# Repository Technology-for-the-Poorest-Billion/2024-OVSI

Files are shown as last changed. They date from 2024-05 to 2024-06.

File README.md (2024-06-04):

# OVSI Usage Monitoring Project

The Oxygen and Ventilator System Initiative (OVSI) "wants to ensure every individual has reliable and equitable access to essential medical oxygen". One of their key innovation domains is in developing a remote monitoring system that can integrate with all types of existing concentrators to track usage and schedule preventive maintenance. Our project looks at performing early stage testing relating to the various different sensors that could be used, and attempting to develop an early prototype. The output from this mini-project should help to give preliminary results and insights into the viablility of the different routes that could be taken to develop a non-invasive monitoring device.

Below is a brief explanation of what is contained in each folder:
- `1. project_proposal` contains both the project proposal and project management information
- `2. interim_report` contains a markdown document containing the interim report for this project
- `3. final_output` contains documentation of the project output which are also the handover notes for the project partner OVSI.
- `4. code` contains all code used throughout the project. It has folders for both the Micropython code used with a Pi Pico and the Python code for reading the output from various sensors through the serial port.
- `5. test_data` contains all of the datasets and results from any testing we performed
- `www` contains the markdown documents which are converted into HTML for our website

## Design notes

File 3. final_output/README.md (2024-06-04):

# OVSI Final Output folder

This folder contains all of the handover notes to be given to Ben and the team at OVSI. This contains a summary of the project, with all the required aspects covered to understand and recreate the prototype. 

Below is a brief explanation of what is contained in each folder:
- `1_prototype_demonstration` contains a demonstration of all functions of the final prototype.
- `2_hardware_and_circuitry` contains the breadboard layout and information on the sensor attachments, including the STL file for the 3D-printed clips.
- `3_code` contains both the Micropython code for the Pi Pico and Python code for reading the output of the sensors through the serial port, and converting it into a live interface.
- `4_further_considerations` contains a markdown document for suggestion for the next steps of the project, including ideas for refinement of the prototype, and further research that could be conducted.
- `5_testing_results` contains the results of the tests performed on the accelerometer and microphone used in producing the final prototype.
- `6_final_presentation` contains a .pdf file containing the slides to our final powerpoint presentation. The .mp4 video of the presentation is too large to attach here, but can be found on the final project submission to the project supervisor.

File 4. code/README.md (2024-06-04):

# Code documentation

The `accelerometer_code` folder contains any code which relates to the testing of the accelerometer.

The `microphone_code` folder contains any code which relates to the testing of the microphone.

The `combined_sensors_code` folder contains any code which relates to the testing of the device when both the accelerometer and the microphone were attached.

All code contains a description of the function of the code at the top of the file.

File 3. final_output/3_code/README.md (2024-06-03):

# Final Prototype Code

This folder contains the code needed to run the final prototype.

`main_combined_sensors.py` contains the micropython code that is used on the Raspberry Pi Pico to take the accelerometer output, and convert it into the accelerometer magnitude. It also takes the analogue microphone signal and converts it into a noise reading on a scale of 1-10.

`final_prototype.py` contains the python code to be used on a laptop to read the Pi Pico output through the serial port. There is a description of the code functionality at the top of the code.

The circuit needed to run the code is shown in the `hardware_and_circuitry.md` file.

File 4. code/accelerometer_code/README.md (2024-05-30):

# Code documentation

The `pico_micropython_code` folder contains the Micropython code that has been used on the Raspberry Pi Pico WH microcontroller. The top of every `.mpy` file will contain a brief description of what the code achieves.

The `python_read_from_serial` folder contains any Python code that reads the output from the serial port when the Pi Pico is attached to a laptop. Every `.py` file will contain a brief description of the purpose of the code at the top of the file, as well as which `.mpy` code it should be run with.

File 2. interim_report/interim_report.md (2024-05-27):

# Interim Presentation

### Work we have achieved to date

- Background reading on other similar applications of non-intrusive load monitoring. 
- Settled on our most promising idea for achieving monitoring using vibration sensing.
- Connected accelerometer to microcontroller.
- Written code to read and manipulate accelerometer data.
- Connected LED circuit to give visual interpretation of data.
- 3D printed mounting solution for breadboard. 
- Tested the vibration readings under a variety of conditions to help determine our measurement approach to monitoring.
- Data analysis of vibration readings.
- Developed and tested some prototype code using Matplotlib to determine and show whether or not the concentrator is on or off.

# Setup and Testing

### Setting up the accelerometer

To allow the Rasberry Pi Pico to read the accelerometer outputs, we first soldered pins onto the accelerometer so that we could connect it to the breadboard. We then attached the pico and accelerometer onto the breadboard and connected them together using jumper wires between the following pins:
 
 - **2-5V** on accelerometer to **3V3(OUT)** on pico.
 - **SDA** on accelerometer to **I2C1 SDA** on pico.
 - **SCL** on accelerometer to **I2C1 SCL** on pico.
 - **GND** on accelerometer to **GND** on pico.

Reading the output:

The next step was to be able to read the outputs from the accelerometer. This was done using an early version of the code main_interim_prototype.mpy and we were able to read the outputs using Thonny. It returned values of the x, y and z components of the acceleration as well as the magnitude.
In order to plot and visualise the accelerometer outputs we used Python in VS Code to read the serial output and create a live plot using the Matplotlib animation function. An example of this plot can be seen in Figure 1 below.

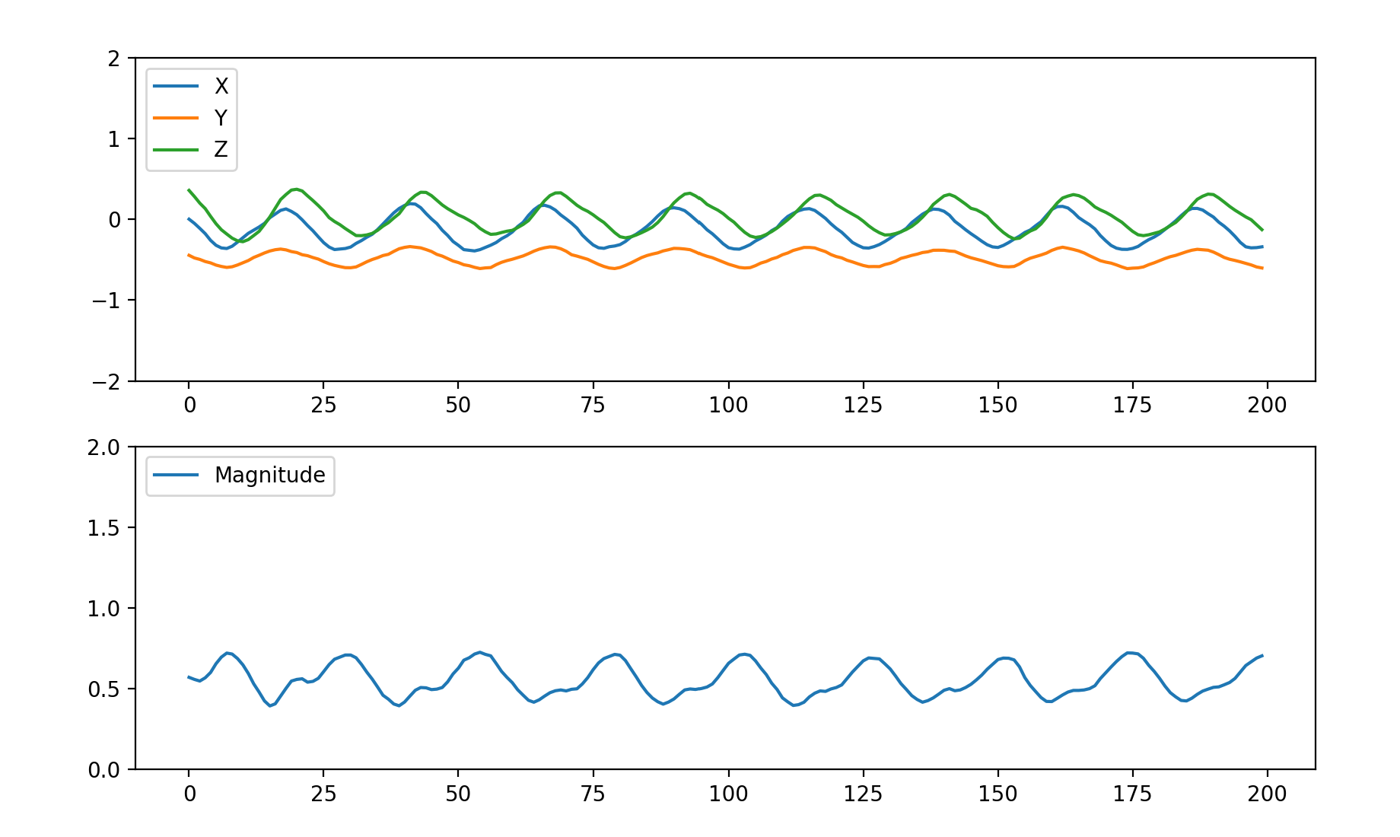
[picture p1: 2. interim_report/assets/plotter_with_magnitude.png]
Screenshot of python plotter


**Figure 1:** Screenshot of the python script plotting the x, y, z components from the accelerometer as well as the magnitude (measured in 'g'). The scale at the bottom shows the last 200 readings (i.e. 2 seconds).

Next we attempted to remove the gravitational component of the reading on the accelerometer by using the inbuilt gyros. We tried various filters and algorithms but were unable to find a simple enough solution, and so to avoid wasting time we decided simply to assume the sensor always remains vertical, and remove a value of 1g from the z output.

### Testing and Results

In order to test our accelerometer under the same conditions each time, it was important to create a system to mount the breadboard to the concentrator. Using a CAD design and 3D printing, we made clips that are glued to the plastic casing and allowed the breadboard to be attached and removed easily. See clip.STL in the assets file.

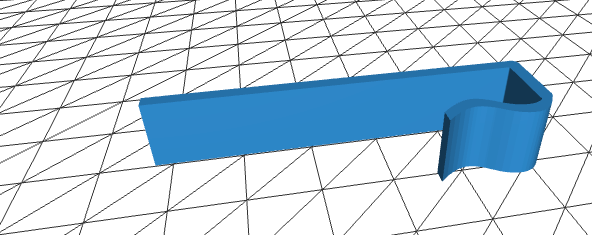
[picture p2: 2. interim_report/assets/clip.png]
clip.STL


We then ran tests to see if we could find a suitable vibration threshold that would indicate if the oxygen concentrator was being used. To do this we ran six different experiments, where we measured the vibrations:
- when the concentrator was turned on
- when the concentrator was turned off with no noise
- when the concentrator with the sensor attached was turned off, but the other concentrator was turned on and touching it
- when the concentrator with the sensor attached was turned off, but the other concentrator was turned on and 10cm away from it
- when the concentrator with the sensor attached was turned off, but we continuously rolled a trolley past and simulated heavy footfall
- when the concentrator with the sensor attached was turned off, but we put the front wheels on blocks to simulate being on uneven ground

Each test was run for 120 seconds. We then took the data and calculated the value of every rolling 10s mean and standard deviation. On the graphs we then plotted the smallest value of the rolling mean and standard deviation for the baseline-on test, and then the largest of the mean and standard deviation for the other test cases. 

Figure 2 below shows the results from when the accelerometer was attached to the black (significantly louder) concentrator. This shows that both the mean magnitude of vibration and the standard deviation when the concentrator is on can be easily differentiated from the other cases. 

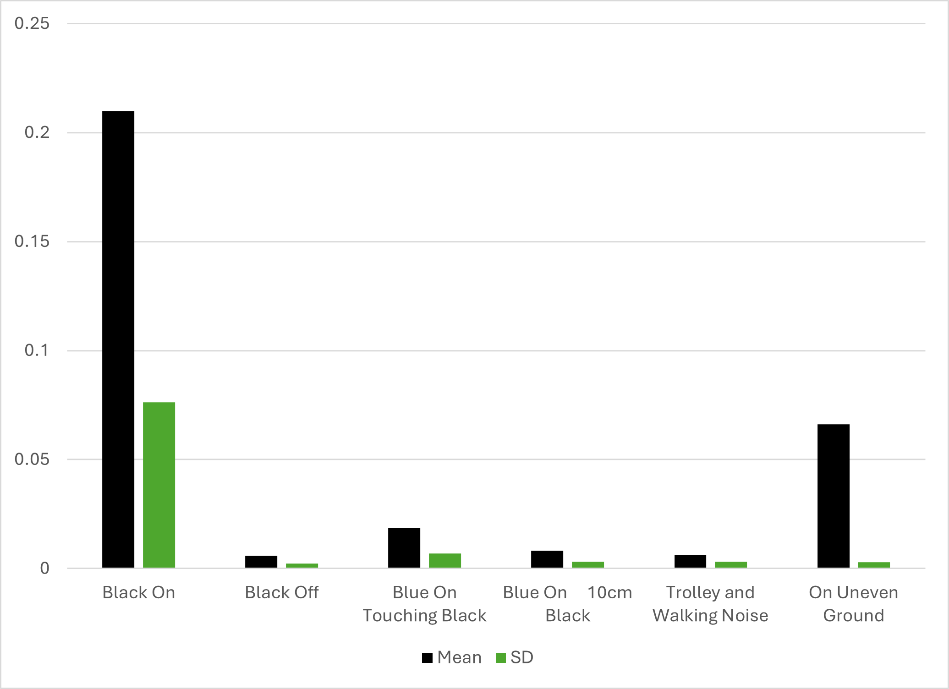
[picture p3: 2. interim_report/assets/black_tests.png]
bar chart of tests on black concentrator


**Figure 2:** Bar chart from the testing performed on the black concentrator.  

However, the Figure 3 below tells a different story. The blue EverFlo concentrator is significantly more quiet - 43dB rather than 69dB for the black one. The most common concentrators used in the target market are 40-50dB, so this is more indicative of the results we would expect to see during service. Here the results show that the mean and standard deviation for the test cases is of a similar or greater magnitude to the baseline-on case. This makes detection more difficult. Having the powerful black concentrator turned on next to the blue one gives comparable values to when the blue concentrator is in the on state and so could give false readings. Furthermore, uneven ground gives large readings for the magnitude, so any unexpected placement of the concentrator could give false readings. Also the standard deviation for the baseline-off test was much larger than expected, and after further analysis this was due to just a few larger values, which shows the ability of short impacts to the concentrator to spike the standard deviation reading.

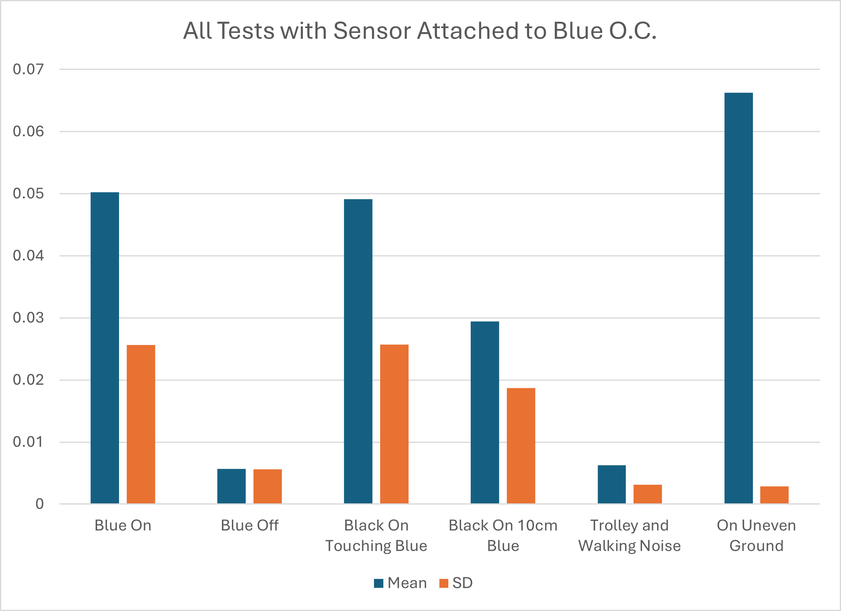
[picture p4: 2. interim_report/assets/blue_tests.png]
bar chart of tests on blue concentrator


**Figure 3:** Bar chart from the testing performed on the blue concentrator.  

Figure 4 shows the relative readings from the tests performed on the two oxygen concentrators, this shows that any strongly vibrating machinery placed nearby to the blue concentrator could result in false readings, whereas for the black concentrator it is much easier to differentiate the on and off state. This is something we plan to test further in order to better understand the likelihood and severity of this case in practice.

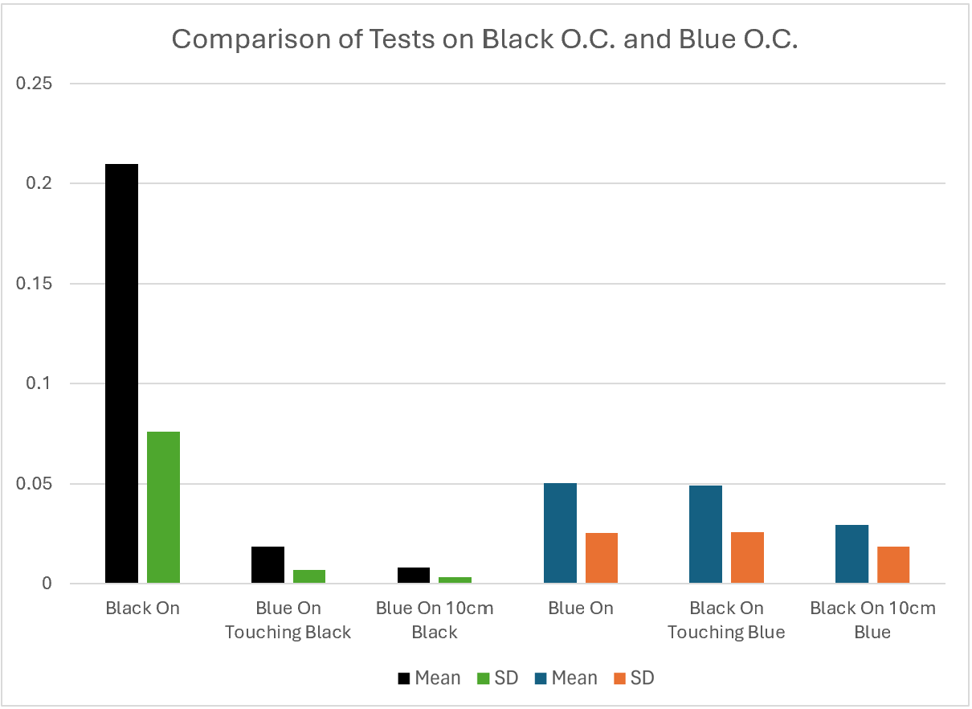
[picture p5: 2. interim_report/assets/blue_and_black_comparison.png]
bar chart comparing tests on black and blue concentrator


**Figure 4:** Bar chart comparing the results from the black and blue concentrators.  

The charts above have clearly demonstrated that being on uneven ground can give large mean value readings but very low standard deviation, as it is a steady state error. A sudden impact on the concentrator is enough to push the standard deviation over the expected value but due to the 10 second moving average it does not cause a dramatic increase in the average magnitude. This resulted in the implementation of a double threshold system where both magnitude and standard deviation were required to be above their threshold value for the device to recognise the concentrator as on. Tests below show the success of this new system.

Using these results we initially attempted to code the double threshold system directly onto the Raspberry Pi Pico, using an integrated LED circuit. Whilst we managed to get it working for the mean threshold, when we added in the standard deviation data we had memory storage issues. For this reason the 'prototype' discussed in the next section takes the accelerometer readings from the serial port and then does all the calculations and analysis in Python on a laptop.

# Prototype

### How it works

- Our 'prototype' Python code takes the readings of the magnitude of acceleration as measured by the accelerometer, and finds the mean and standard deviation of the last 1000 readings (i.e. 10 seconds).
- Every time a new reading comes in, the mean and standard deviation values are updated and then compared to a threshold. The thresholds have been determined from the testing done in the previous section. These thresholds determine whether or not the code thinks that the concentrator is currently turned on or off.
- In order to visualise this information, we have used the Matplotlib.animation function to plot the updated mean and standard deviation every time a new reading is taken. The plot shows the last 200 updated readings.
- The thresholds that are set for the mean and standard deviation are also plotted on the graph for easy viewing. When both thresholds are met the screen will turn green to show that the oxygen concentrator is running. If one or both of the outputs are below their respective thresholds then the screen will be red, indicating that the concentrator is not running. 

### Demonstration
All of the following data and graphics have been produced from testing performed with the accelerometer attached to the blue oxygen concentrator (the quieter of the two).
Figure 5 shows the Matplotlib output when the blue concentrator is turned on. Both the mean and standard deviation of the accelerometer readings are above the predetermined threshold and so the screen has turned green.

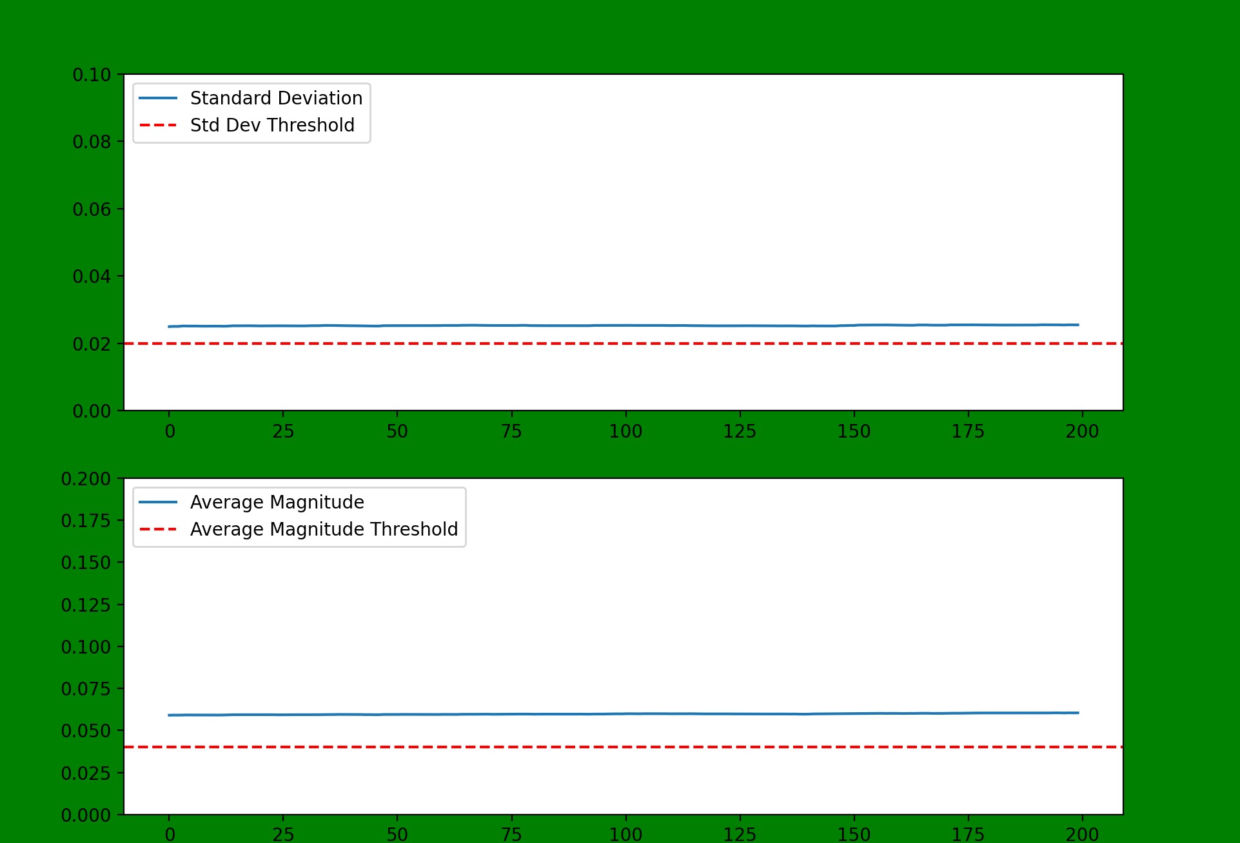
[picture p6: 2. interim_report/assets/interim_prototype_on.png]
screenshot of prototype with blue conc on


**Figure 5:** Prototype output when the blue concentrator is turned on.  

Figure 6 shows how the mean and standard deviation are affected by large knock to the concentrator. This noise is enough to send the standard deviation reading well over the threshold, but the mean stays comfortably below, and so the screen stays red.

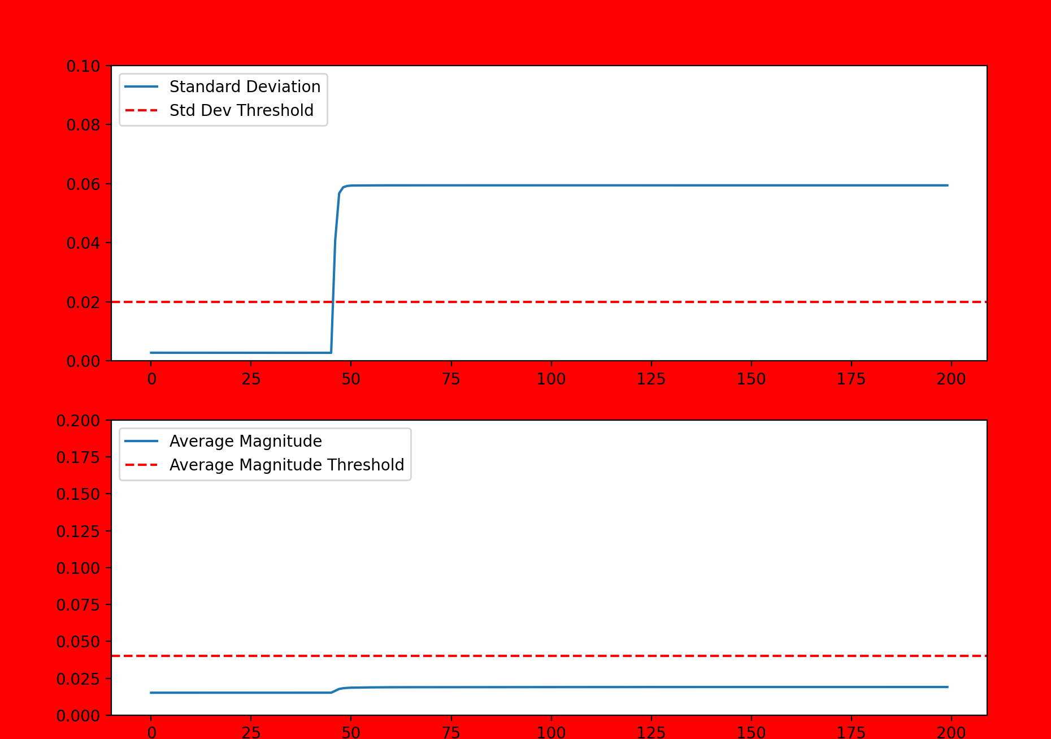
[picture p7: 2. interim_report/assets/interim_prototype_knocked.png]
screenshot of prototype with knock


**Figure 6:** Prototype output when the blue concentrator is turned off and knocked.  

Figure 7 shows the effect of leaving the concentrator on an uneven surface and during this measurement the concentrator was turned off. It is clear that the mean reading is well above the threshold due to gravity affecting the accelerometer readings. However, the standard deviation remains close to zero and so because this threshold is not met, the screen remains red.

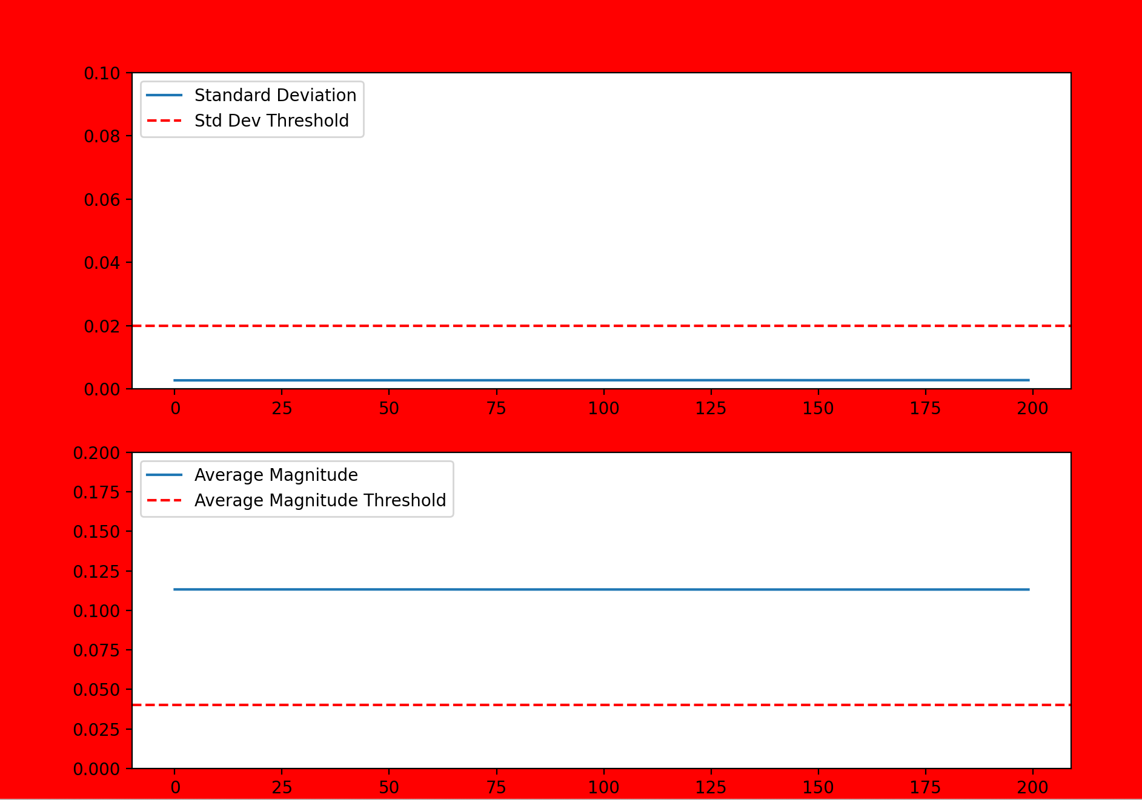
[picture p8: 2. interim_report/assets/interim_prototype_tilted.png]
screenshot of prototype with blue on tilt


**Figure 7:** Prototype output when the blue concentrator is turned off and placed on uneven ground.  

Figure 8 shows the Matplotlib interface when the blue concentrator is turned off, but the noisy black concentrator is turned on next to it and making direct contact. Whilst the readings are clearly above zero neither threshold is met and so the screen is red to show that the concentrator is not running.

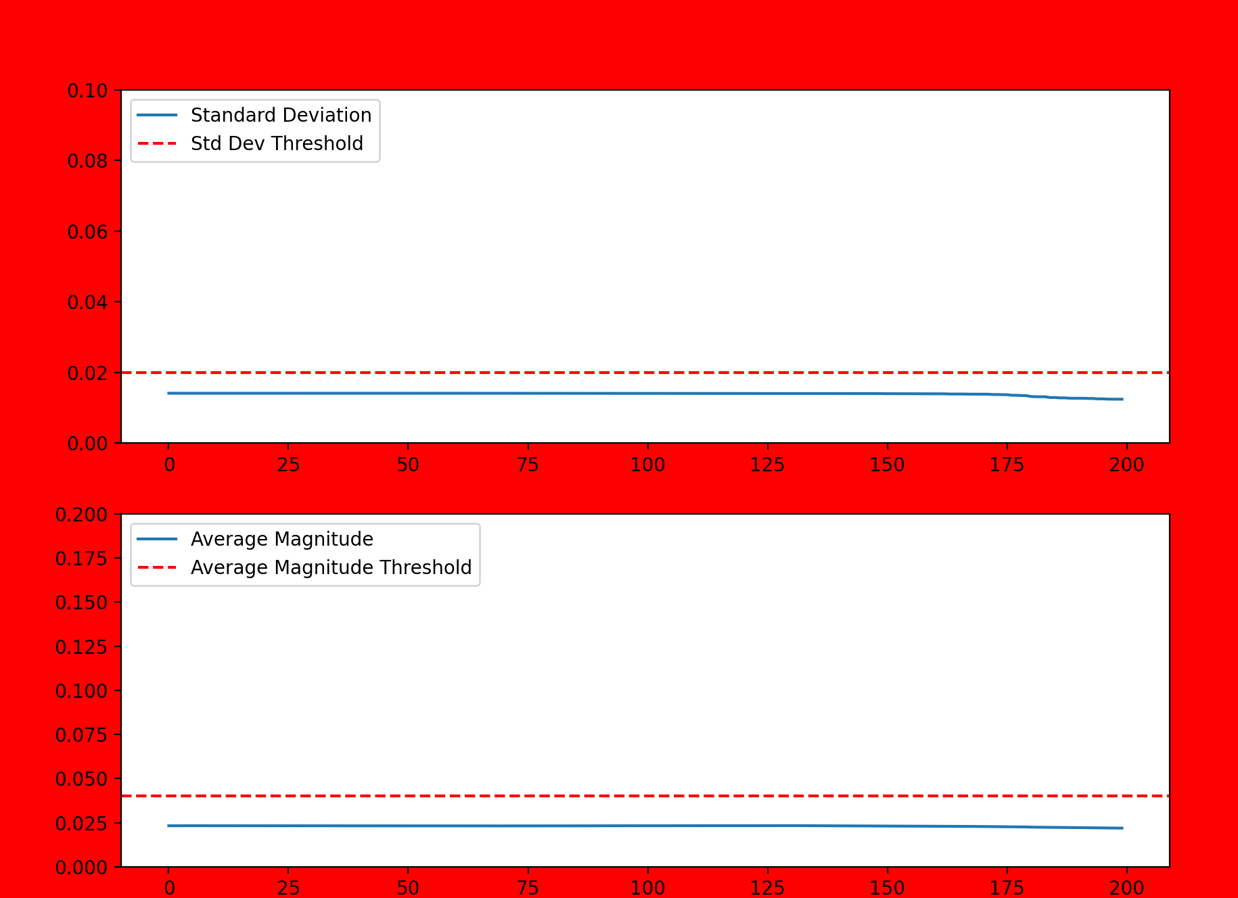
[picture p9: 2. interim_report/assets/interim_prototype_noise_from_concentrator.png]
screenshot of prototype with black on next to blue


**Figure 8:** Prototype output when the blue concentrator is turned off, and the black concentrator is turned on and touching. 

Below is a demonstration video of the above tests being performed.

https://github.com/Technology-for-the-Poorest-Billion/2024-OVSI/assets/98593139/cfc9f4a7-5daf-4990-bf7b-f4c7b06e2e5d

By using python to manipulate and plot the readings from the accelerometer it allowed for much easier analysis of how the monitoring system was working. However, once we had the above system in place, it was possible to try and convert the concept back into MicroPython code and use it alongside the LED circuit once again. This is now running successfully, and follows the exact same concept as the above prototype. Figure 9 below shows a photo of the setup, whereby the green LED lights up when both the mean and standard deviation values are above the threshold.

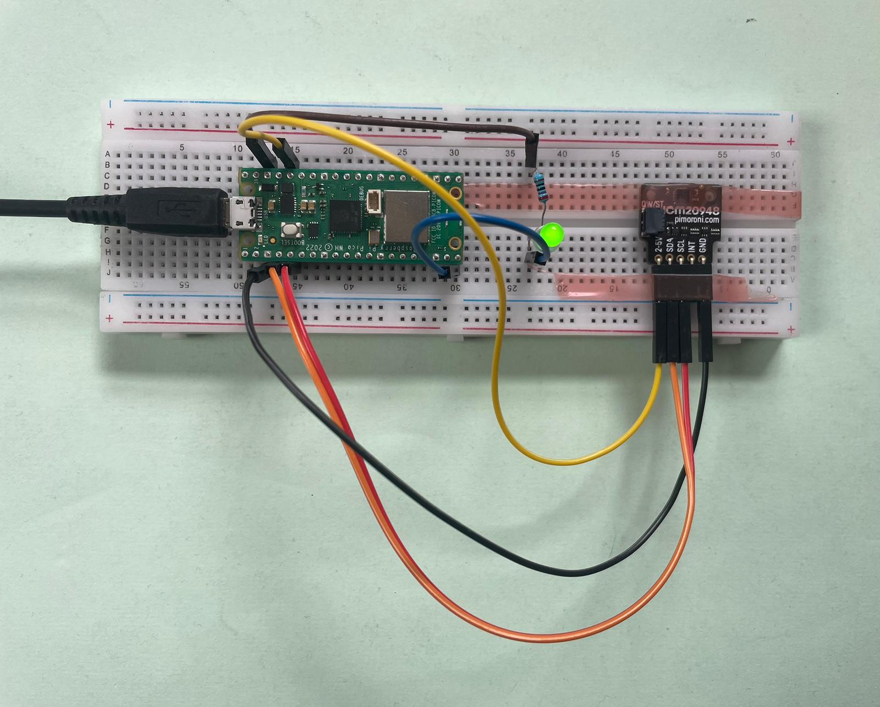
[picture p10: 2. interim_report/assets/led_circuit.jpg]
photo of led breadboard set up


**Figure 9:** Breadboard with Raspberry Pi Pico, accelerometer sensor and LED circuit.

### Prototype alignment with project objective
This prototype aligns well with the project objective which was to test the suitability of different sensors for use in monitoring an oxygen concentrator. We have run various tests to assess how the accelerometer could be used as part of a monitoring device. We have not had much to consider in terms of the context in which the device will be applied due to the fact that we are simply looking at the information that the sensor can provide. However, our final output will contain a list of considerations for Ben and the team as they begin to construct an actual monitoring device, to ensure it will be appropriate for the final environment that it will be used within.

# Project management

### Issues and steps to overcome

- First microphone sensor gave poor data and so we reshuffled the schedule to focus on vibration monitoring until a new sensor was delivered 3 days later. 
- The initial Matplotlib.animation plot was severely lagging due to the fact that it was attempting to update the plot every time a new value was read. To overcome this we added in a buffer which stored the values to be plotted, and then separately updated the plot at a more achievable rate using the values stored in the buffer.
- The output was failing to include all of the incoming values from the serial port. This is because initially the reading of the data was being performed inside the loop which was operating more slowly than the speed of the incoming data. To overcome this we added a separate thread which was able to add the serial output readings to the buffer in the background, whilst the main code could continue to manipulate the data and update the plots.
- We initially had problems performing the required calculations directly on the pico itself, which is why we resorted to doing it in python, so that we could continue with our testing without getting behind schedule. We eventually managed to get the LED code working on the pico again, and so we could transfer what we had done in python into MicroPython.
- As mentioned above we aimed to remove the gravitational component of the reading on the accelerometer by using the inbuilt gyros. We tried various filters and algorithms but were unable to find a simple enough solution, and so to avoid wasting time we decided simply to assume the sensor always remains vertical, and remove a value of 1g from the z output.
- During testing we found that uneven surfaces gave accelerometer magnitude readings that were above the threshold value. We also found that some unexpected noise during our baseline off test pushed the standard deviation much closer to the threshold level than we were expecting. Because of these two findings we settled on using a double threshold of mean and standard deviation to eliminate false readings. This then gave the correct monitoring status for all of the data that we recorded during testing.

### Personal and technical development

Harry: 

- Learnt about the climate we are implementing our solution into. 
- Learnt how to connect different sensors to a variety of microcontrollers and how to wire an LED circuit. Self taught from online manuals.
- Learnt how to solder connections with help from a technician in the Dyson centre.
- Learnt how to use the 3D printer to make the clips. 

Alex:

- Reminder of how microcontrollers work using online resources and datasheets.
- Learnt how to program a Raspberry Pi Pico using MicroPython and Thonny.
- Learnt how to read from the serial port using python.
- Learnt how to use Matplotlib.animation to produce live plots.
- This has all been self taught using various online sources.
- Improved my resilience to the constant issues that I faced during coding

### Updated project development timeline 

- Week 1: Understanding the problem and identifying potential solutions.
- Week 2: Setup of vibration monitoring prototype and successful testing. 
- Week 3: Sound monitoring feasibility test, refinement of vibration prototype. 
- Week 4: Documenting our envisiged next steps for the development of the monitoring system. Submitting project deliverables.

Slight reshuffle due to a delay in sound sensor arriving but overall ahead of schedule.

### Plan for project completion 

- Initially looking to spend 2 days maximum testing the new microphone sensor. If early results seem promising then we can continue with further testing, otherwise we will focus on further development of the accelerometer setup.
- Further analysis of test data for vibrations to set a more robust design threshold. Looking to perform further experiments such as testing on different floor surfaces and trying to find various realistic sources of random noise.
- Run longer duration tests to establish better accuracy.
- Decide if degradation monitoring is feasible in the remaining time.
- Create a document of next actions and key feedback for Ben, based off the project findings.

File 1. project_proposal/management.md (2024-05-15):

# Project Management Plan

## The people

Harry Antill & Alex Beeston

**Strengths:**
- Mechanical and materials engineering. 
- Successful previous project experience together.

**Weaknesses:**
- Electrical and software engineering.
- Knowledge of microcontrollers and sensor integration.

**Skills Required:**
- Critical understanding of the cultural and operational environment where the technology is needed.
- Ability to work with various stakeholders from different backgrounds.
- Analytical skills to judge the effectiveness of solutions.
- Ability to create rapid prototypes and quickly assess functionality. 
- Programming and understanding of data storage and transfer.
- Project management skills (resource coordination and risk management).
- Technical writing and presentation skills.

**Training Needed:**
- GitHub.
- Microcontrollers and sensors.
- Data storage and transfer processes.
- Potentially CAD modelling.
- Potentially 3D printing.

## The resources needed

**From Ben Moore:**
- Oxygen Concentrator (1 or 2).
- Sensors and other assortment of parts for testing of physical solutions.

**Externally Sourced:**

Will evolve as ideas are refined but likely to include:
- Sensors.
- Casing parts.
- 3D printed housing.
- Bolts and other joining components.
- Cheap basic microcontroller.
- Wiring and solder metal.

Total budget likely in region of £100. 

## The timeline

**Tasks:**
- Week 1: Understanding the problem and identifying potential solutions.
- Week 2: Initial testing of most promising ideas.
- Week 3: Tangible solution to usage monitoring with testing and modifications.
- Week 4: Attachment to the concentrator and degradation monitoring.

## The assessment of the risks and safety

**Risks:**
- Tools used for physical manufacture can be sharp. Mitigated by using suitable protective equipment and having suitable training on relevant equipment.
- Live electrical components. Do not make changes whilst connected to the power source.
- Transport of large oxygen concentrator machines. Lift in pairs where necessary. 

## Contingency plans

**Potential Pitfalls**
- Prototype of solution is not achievable within timeframe. 
- Difficulty sourcing appropriate sensors or resources.

**How to overcome**
- If prototype not achievable then have CAD model and rigorous optioneering document to give insight into the best approach to the problem.
- If physical resources delayed, make CAD model and prepare manufacture plan to streamline process when they do arrive. 
- We have many avenues for getting resources, both online or through Ben Moore who has funding for the project.

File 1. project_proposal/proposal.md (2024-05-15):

# Problem description

"Pneumonia kills more children than any other infectious disease, claiming the lives of over 700,000 children under five every year... almost all of these deaths are preventable" - UNICEF [2024]. It has been shown that in countries with robust oxygen systems, hospital-based pneumonia deaths can be reduced by half. However, due to the harsh operating environment in Sub-Saharan Africa and South East Asia where pneumonia is most prevalent, these oxygen concentrators often fail to operate reliably.

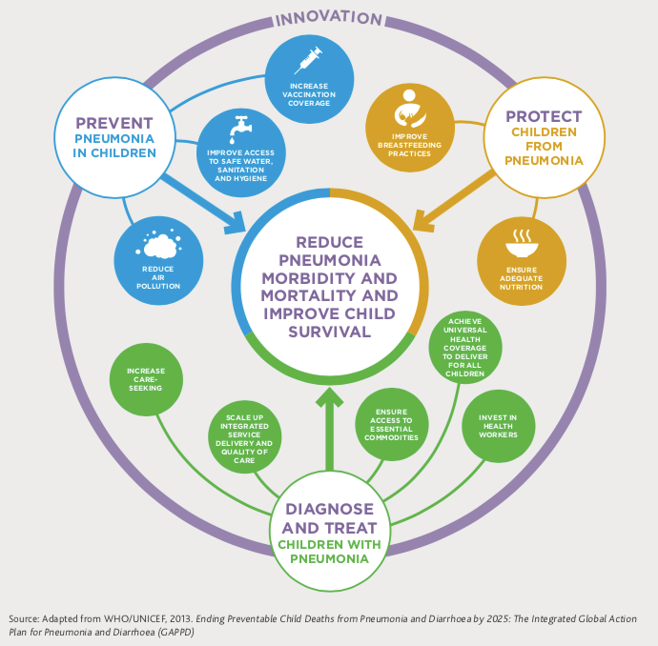
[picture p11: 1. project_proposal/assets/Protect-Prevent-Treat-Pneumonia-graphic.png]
Plan to reduce pneumonia.


The graphic above shows that there are three main 'pillars' that can help to reduce pneumonia related deaths in children: prevention, protection and treatment. As mentioned previously and shown in the graphic, one of the main ways that the treatment of children with pneumonia can be improved is by ensuring that everyone has access to essential commodities - such as oxygen. However, one of the main challenges for Ministries of Health is having the ability to collect meaningful data about the usage and operational status of their oxygen concentrators. If they were armed with this data it would help them to identify the needs and gaps of oxygen supplies in their country, and be able to deal with repair and maintenance more efficiently.

A study by Bradley et al. [2015] on oxygen concentrator maintenance in The Gambia estimates that with the correct preventive maintainance the useful lifespan of these concentrators in low-resource settings could exceed 7 years. The preventive maintenance (PM) checks often resulted in minor repairs having to be carried out, which were generally low-cost and required a low level of experience to complete. This demonstrates that if the usage of a fleet of oxygen concentrators could be accurately measured and recorded, that it could help to schedule PM checks at the optimal times in the lifespan of each concentrator. The study noted that "forty-one per cent of faults needing repair were discovered during PM checks, which likely mitigate more serious or costly future breakdowns and lengthy equipment outages".

It is clear therefore that a simple, low-cost and reliable device that could be implemented to measure the usage of any commercially available oxygen concentrator would be a huge benefit to both biomedical engineers and the Ministries of Health. It would allow for better management and allocation of oxygen concentrators throughout a region, to ensure that all concentrators are being used to maximal effect. By helping to better schedule PM it could also reduce the downtime of the oxygen concentrators and help to catch issues before they escalate into major and costly failures.

# Presentation of the proposal

This project aims to design a reliable and non-invasive monitoring device that is capable of recording the operational status of an oxygen concentrator and that is suitable for use in low-resource settings. 

### The main aims of the project will be to:

- Test various sensors and evaluate their effectiveness given the context that the device will be used in, in order to determine the best choice for the given requirements. The sensor will be used to determine whether or not the concentrator is currently running.  
- Perform degradation testing, to see if any of the sensors would be suitable to try and predict whether any maintenance/repairs will be necessary in the near future.  
- Think about how the monitoring device will attach onto the oxygen concentrators. There are multiple different brands of concentrators all with slightly varying designs, and the device should be made to be compatible with all versions without the need for alterations.  

### Additional aims if time allows:

- Look at how the data from the monitoring device would be stored and collected by the hospital workers.  
- Think about how the device could be used to show that an oxygen concentrator is currently in need of repair, so that data on the number of currently broken concentrators can also be collected.
- Investigate the existing infrastructure in the countries that this device is being designed for and then research a suitable method for collecting and transferring the data to the relevant people.

### Initial scope:

From a brainstorm of potential usage monitoring methods we arrived at the following overarching methods:

- Vibrations --> accelerometer fixed to outer casing will detect usage. It also has the potential to detect changes in frequencies, which could indicate faults.

- Power outlet --> current and/or voltage monitoring to detect usage data, however cannot be invasive i.e. become part of the medical device. 

- Noise --> oxygen concentrators operate above 40dB which is comparable to a quiet refrigerator and so interference in a busy hospital could be an issue. However it has the potential to be the cheapest sensor and could give a wide range of information about faults as well as identifying fault alarms from the concentrator, something the vibration sensor would be incapable of.

- Magnetic field --> the motor for the compressor will result in a magnetic field, however this is more likely to involve an invasive solution to measure the magnetic field and an ideal solution does not require the machine to be tampered with.

- Nitrogen output sensor --> flow would indicate the concentrator is in use and then partial pressure of nitrogen at the outlet would indicate how pure the oxygen is and hence give more detailed insight to the machine health. 

The most feasible sensor choices for this project appear to be vibration and noise with the resources available. We will source a microcontroller that is able to interpret data from either an accelerometer or a microphone to determine whether the machine is operational or not. Based on these results we will choose the best suited approach to the problem given the operating environment. We will proceed with further testing and development to give more insightful feedback and decide how to fix the device to the concentrator considering the optimal position for functionality and practical use.

# Assessment of the quality of the proposal

The Oxygen and Ventilator System Initiative (OVSI) "wants to ensure every individual has reliable and equitable access to essential medical oxygen". One of their key innovation domains is in developing a remote monitoring system that can integrate with all types of existing concentrators to track usage and schedule PM. Our proposal fits in well with this key aim, as it looks at doing early stage testing relating to the various different sensors that could be used and seeking out the potential of these sensors to detect any degradation of an oxygen concentrator. The output from this mini-project should help to give preliminary results and insights into the viablility of the different routes that could be taken to develop a non-invasive monitoring device.

### Key inclusive innovation principles/characteristics:

**Standards and Regulations** - The device should be non-invasive in nature so that it easily meets the strict European standards and regulations that surround the use of medical devices.  
**Collaboratively co-created** - The design process should involve all the stakeholders - particularly the end-users - to ensure that the device is both culturally and contextually appropriate.  
**Enhance agency** - The device should give better control to biomedical technicians and Ministries of Health over the effective use of oxygen concentrators and ensure that they will be able to manage and maintain the technology independently.  
**Low cost** - The design process must consider the initial cost (capex), the operating cost (opex), but also the potential monetary savings from the introduction of a simple and efficient monitoring system.  
**Context appropriate** - The device should be robust, reliable and easy to repair with consideration to the specific environmental conditions it will face.  
**Existing ecosystems** - The device must be designed in such a way that all of its functionality, from the way that it is powered to the way that it stores and transfers data, is able to fit in with the existing infrastructure.  

## References
UNICEF, [2024]. *Pneumonia in Children Statistics - UNICEF DATA*. Available at: https://data.unicef.org/topic/child-health/pneumonia/#:~:text=Pneumonia%20kills%20more%20children%20than,of%20these%20deaths%20are%20preventable.

Bradley B., Chow S., Nyassi E., Cheng Y., Peel D. and Howie S.R.C., [2015]. *A retrospective analysis of oxygen concentrator maintenance needs and costs in a low-resource setting: experience from The Gambia*. Health and technology, 4(4), pp.319–328.

‌

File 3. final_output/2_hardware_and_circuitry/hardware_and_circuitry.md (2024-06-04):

# Circuitry for Final Breadboard Layout

### List of components

- Breadboard
- Raspberry Pi Pico WH
- ICM20948 9DoF Motion Sensor Breakout
- SparkFun Analog MEMS Microphone Breakout - SPH8878LR5H-1
- 10 kΩ resistor
- Jumper wires X 10
- 6mm button
- Header pins

### Connections

Initially the header pins were soldered to the accelerometer and microphone sensors to allow connections to the Pi Pico. The connections between the Pi Pico and the sensors are as follows:

 - **2-5V** on accelerometer to **3V3(OUT)** on pico
 - **SDA** on accelerometer to **I2C1 SDA (GP2)** on pico
 - **SCL** on accelerometer to **I2C1 SCL (GP3)** on pico
 - **GND** on accelerometer to **GND** on pico

 - **VCC** on microphone to **3V3(OUT)** on pico
 - **GND** on microphone to **GND** on pico
 - **AUD** on microphone to **I2C1 SDA (GP26)** on pico

 - **One leg** of the switch to **(GP15)** on pico
 - **Opposite leg** of the switch to **GND** on pico
 - A 10 kΩ resistor connects **GP15** to **live rail** 

Where a pin number is specified in brackets it is required to be compatible with existing code but any GPIO pin will suffice.

Where testing of each sensor separately has been performed, the same pin connections were used.

Raspberry Pi Pico WH datasheet:

https://datasheets.raspberrypi.com/picow/pico-w-datasheet.pdf , Accessed: (03/06/2024)

### Circuit setup schematic

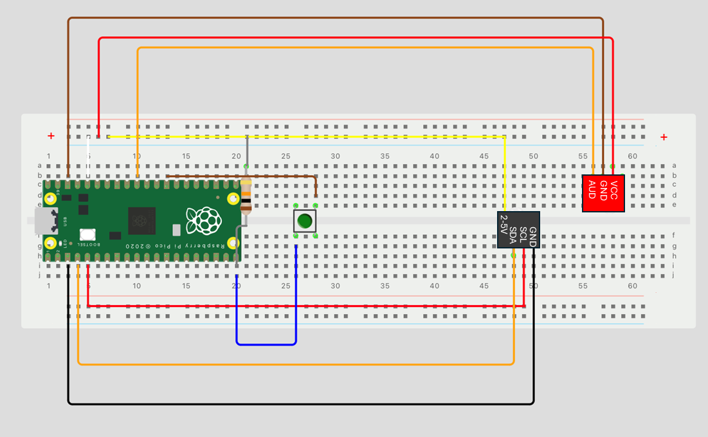
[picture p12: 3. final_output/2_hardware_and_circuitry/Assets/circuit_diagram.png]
Circuit diagram


The microphone is shown attached to the breadboard for the purpose of the schematic, but tests were run with it inside a separate casing but still wired to the pico with the connections as shown. The casing is shown in later sections.

# Mounting solutions

### Breadboard attachment

In order to run tests reproducibly and to be able to quickly mount and dismount the breadboard for alteration, we designed custom clips. These were 3D printed from PLA filament after SolidWorks modelling. The STL file for the [clip](</3. final_output/2_hardware_and_circuitry/Assets/clip.STL>) is shown in the Assets folder. Two clips were used per concentrator, superglued to a flat surface of the plastic casing. See [further considerations](</3. final_output/4_further_considerations/>) for how this can be improved.

### Sound isolation for microphone sensor

As seen in [testing](</3. final_output/5_testing_results/>), initial microphone tests were not promising for differentiating between concentrator sound and background noise. In order to rectify this, a solution was required to isolate the concentrator noise and exclude external noise. 
To do this as a rapid prototype, the sensor was taped to the inside of a box with a hole facing the concentrator. The box was then filled with foam to exclude external noise. The setup is shown below with the box open for aid of visualisation:

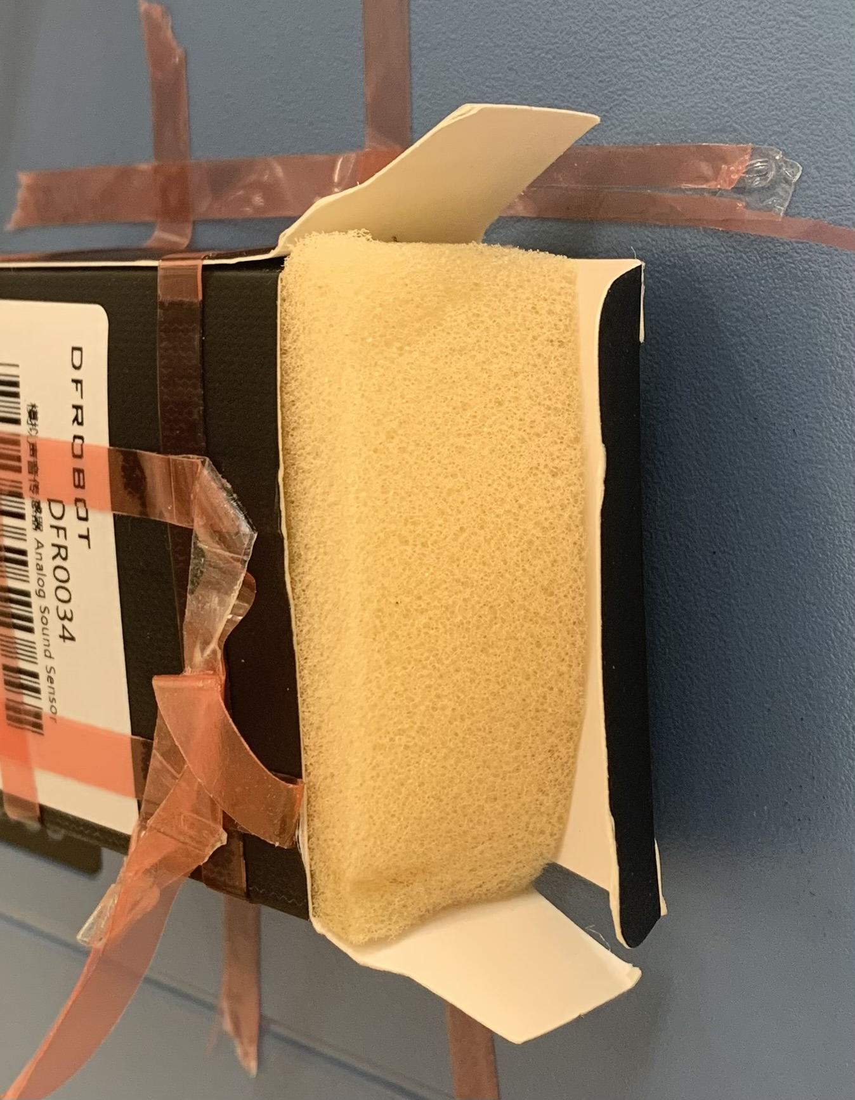
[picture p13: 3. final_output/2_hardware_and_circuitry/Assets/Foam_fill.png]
Microphone noise isolation


The data for the success of this setup is shown in the `5_testing_results` section.

# Concentrator testing

### Concentrators used for testing

We were using two concentrators for testing: 

- Drive Devilbiss 10 Litre Compact Oxygen Concentrator 1025 
- Philips Respironics EverFlo 5L Oxygen Concentrator

They are both on the upper end of the price range, but the Philips concentrator well resembled the concentrators that are used in practice, both in terms of its output(5L) and its noise level (43dB). The most common concentrators that we are designing this device for are in the 40-50dB range. The Devilbiss concentrator is reported at 69dB operational noise level. This made it a useful worst-case scenario for many of our interference tests, where we would monitor the quiet concentrator with the loud one running nearby. 

### Final Setup 

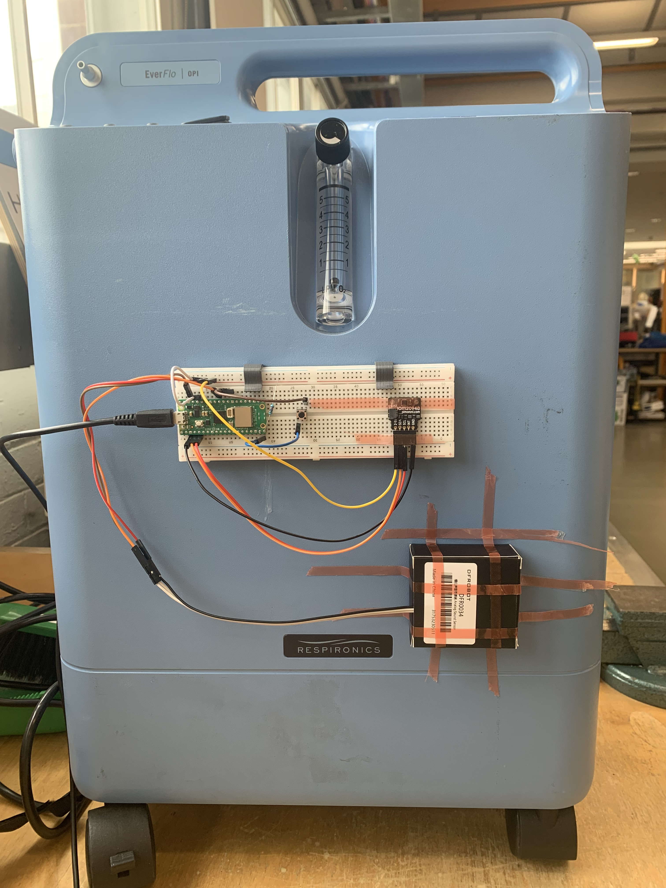
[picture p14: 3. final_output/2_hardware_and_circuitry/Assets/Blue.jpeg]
Final setup on EverFlo


The micro usb is connected to a laptop which uses Thonny to code the Raspberry Pi Pico WH, and Python to read the accelerometer and microphone outputs through the serial port.

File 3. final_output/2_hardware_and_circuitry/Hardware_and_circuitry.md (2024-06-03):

# Circuitry

Final prototype breadboard setup. 

### List of components

- Breadboard
- Raspberry Pi Pico WH
- ICM20948 9DoF Motion Sensor Breakout
- SparkFun Analog MEMS Microphone Breakout - SPH8878LR5H-1
- 10 kΩ resistor
- Jumper wires X 10
- 6mm button
- Header pins

### Connections

Initially the header pins were soldered to the accelerometer and microphone sensors to allow connections to the Pi Pico.

 - **2-5V** on accelerometer to **3V3(OUT)** on pico
 - **SDA** on accelerometer to **I2C1 SDA (GP2)** on pico
 - **SCL** on accelerometer to **I2C1 SCL (GP3)** on pico
 - **GND** on accelerometer to **GND** on pico

 - **VCC** on Microphone to **3V3(OUT)** on pico
 - **GND** on Microphone to **GND** on pico
 - **AUD** on Microphone to **I2C1 SDA (GP26)** on pico

 - **One leg** on Switch to **(GP15)** on pico
 - **Opposite leg** on Switch to **GND** on pico
 - Resistor connects **GP15** to **live rail** 

Where a pin number is specified in brackets it is required to be compatible with existing code but any GPIO pin will suffice.

For testing of each sensor separately as the same pin connections were used.

Raspberry Pi Pico WH datasheet:

https://datasheets.raspberrypi.com/picow/pico-w-datasheet.pdf , Accessed:(03/06/2024)

### Circuit setup schematic

Circuit diagram

The microphone is shown attached to the breadboard for the purpose of the schematic, but tests were run with is inside a separate casing but still wired to the pico. This is shown in later sections.

# Mounting solutions

### Breadboard attachment

In order to run tests reproducibly and be able to quickly mount and dismount the breadboard for alteration, we designed custom clips. These were 3D printed from PLA filament after SolidWorks modelling. The STL file for the [clip](</3. final_output/Hardware_and_circuitry/Assets/clip.STL>) is shown in the Assets folder. Two clips were used per concentrator, superglued to a flat surface of the plastic casing. See [further considerations](</3. final_output/Further_considerations/>) for how this can be improved.

### Sound isolation for microphone sensor

As seen in [testing](</3. final_output/Testing/>) initial microphone tests were not promising for differentiating between concentrator sound and background noise. In order to rectify this, a solution was required to isolate the concentrator noise and exclude external noise. 
To do this as a rapid prototype, the sensor was taped to the inside of a box with a hole facing the concentrator. The box was then filled with foam to exclude external noise. The setup is shown below with the box open for aid of visualisation:

Microphone noise isolation

The data for the success of this setup is shown in the testing section.

# Concentrator testing

### Concentrators used for testing

We were using two concentrators for testing: 

- Drive Devilbiss 10 Litre Compact Oxygen Concentrator 1025 
- Philips Respironics EverFlo 5L Oxygen Concentrator

They are both on the upper end of price, but the Philips concentrator well resembled the concentrators used in practice in term of its output(5L) and its noise level (43dB). The most common concentrators that we are designing for are in the 40-50dB range. The Devilbiss concentrator is reported at 69dB operational noise level. This made it a useful worst-case scenario for many of our interference tests, where we would monitor the quiet concentrator with the loud one running nearby. 

### Final Setup 

Final setup on EverFlo

The micro usb is connected to a laptop which uses Thonny to code the Raspberry Pi Pico WH, and Python to read the accelerometer and microphone outputs through the serial port.

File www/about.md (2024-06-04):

---
title: Our Prototype
---

Our project addresses a critical healthcare challenge: ensuring reliable access to medical oxygen in low-resource settings to treat pneumonia in children. For this reason, we developed a prototype device which can be used to monitor the operational status of oxygen concentrators, which are essential medical resources for treating pneumonia, but often fail due to harsh operating conditions.

Our monitoring system uses sensors to track whether an oxygen concentrator is running. We tested various sensors and decided on a combination of an accelerometer and a microphone. These sensors measure the level of vibrations and noise, respectively. The prototype device uses a threshold-based system, where three conditions must be simultaneously met for the concentrator to be confirmed as running, which are all determined based off the information that the sensors are returning to the device.

#### **Robust Against Noise**

We demonstrated the resilience of our prototype to several test-cases:

- In all of the tests that were performed, when the concentrator was on and running, the device was able to correctly display this status 100% of the time.
- Of the eight simulations performed to test the monitoring device under different operating conditions, it proved to be robust against external noise in all but one case. With further testing and refinement of the model, as well as incorporating smart machine learning algorithms, it is hoped that the device will eventually be resilient to all types of interference.

#### **Universally Compatible**
- The device has in-built calibration capabilities, so that the thresholds can be set to ensure that the device is compatible with any brand of oxygen concentrator.
- With the press of one button, it then only takes ten seconds to ensure the device is optimally set up to work with the required oxygen concentrator.

#### **Clear Visual Cues**

The device's status is displayed using a simple colour-coded system:

Red: The concentrator is off.  
Orange: The device is in calibration mode.  
Green: The concentrator is on and running.

#### **The Prototype**

Below is an image of the prototype during testing, attached to a typical oxygen concentrator. The final device will contain all of the sensors and components in a simple yet effective housing, which will protect them from the harsh environmental conditions.

photo of prototype

#### **Further Information**

For those more interested in the inner workings of the project, the photo below shows the prototype going through the calibration process. It starts off misinterpreting the concentrator as being turned off (as the deivce has not been calibrated to this particular concentrator yet), as shown by the red screen. Next, the button is pressed to begin the threshold calibration of the device, as shown by the orange display. Finally, once calibration has been completed, the device is now correctly monitoring the oxygen concentrator as up and running, as shown by the green interface!

The three white plots on each screen show the three sensor outputs that are being monitored, and these outputs are represented via the blue line. The thresholds are represented by the red dashed line. All three thresholds must be met for the oxygen concentrator to be determined as running!

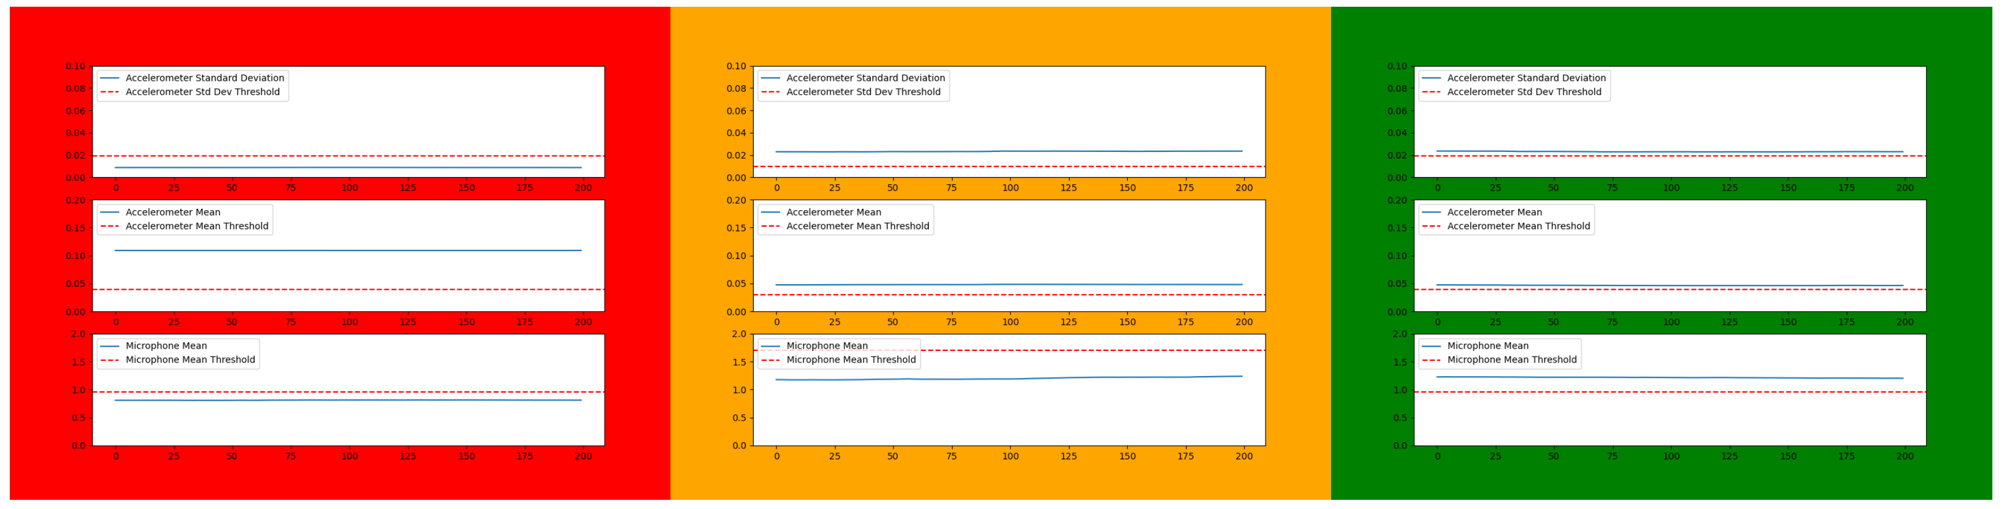
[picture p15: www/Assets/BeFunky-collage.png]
screenshot of prototype code


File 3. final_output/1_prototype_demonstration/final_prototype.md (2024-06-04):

# Final Prototype Demonstration

Following prior testing as documented in `5_testing_results`, we had decided that our monitoring system would use a threshold-based system, whereby all three thresholds have to be met in order to signal that the concentrator is running. These three thresholds are related to:
- a 10 second rolling mean of the accelerometer magnitude
- a 10 second rolling standard deviation of the accelerometer magnitude
- a 10 second rolling mean of the microphone magnitude

In order to display the current status of the monitoring system in the figures below, the following colour coding is used:
- red signals that the concentrator is not running
- orange signals that the monitoring device is undergoing threshold calibration
- green signals that the concentrator is running

The below figures now run through an example test of the monitoring system. The x-axes show the last 200 readings (2 seconds) of each of the three measures discussed above. The y-axes for the accelerometer plots are measured in 'g'. For the microphone plot the y-axis is measured in 'volume  units', which is a scale from 0-10 of the range of noise that the microphone is capable of measuring.

Figure 1 shows a screenshot of the output when the device has just been turned on. The concentrator it is attached to is turned off, and there is only quiet background noise. The thresholds shown are presets based off typical concentrator characteristics, but they have not been calibrated to the particular concentrator. The screen is red showing that the device is recording the concentrator as being turned off.

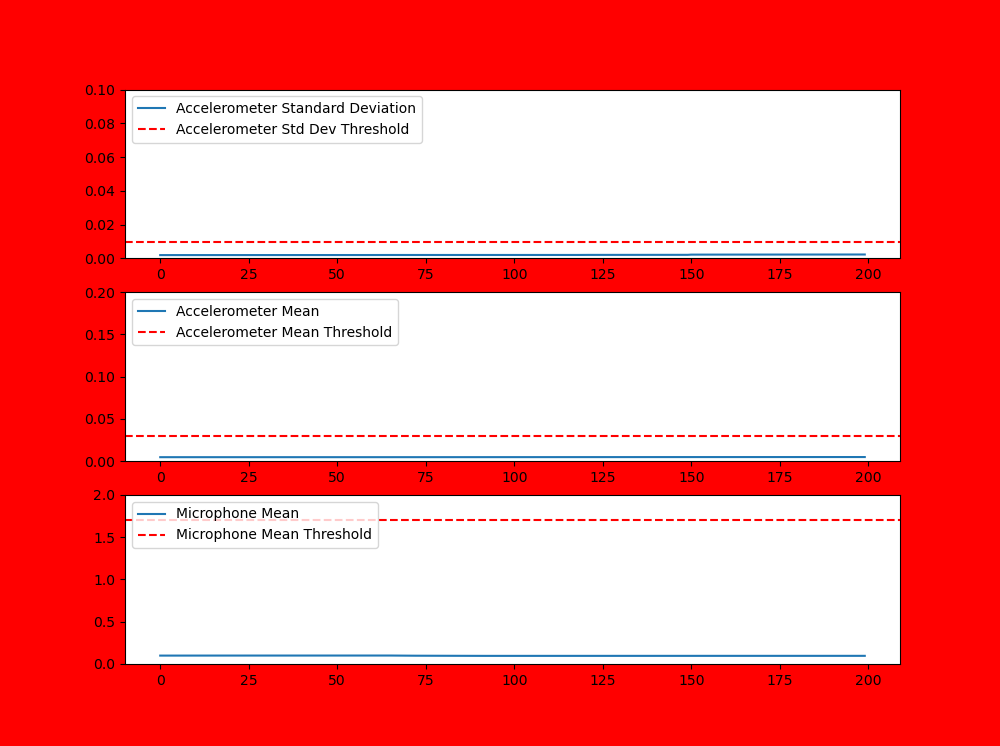
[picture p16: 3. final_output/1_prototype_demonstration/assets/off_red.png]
prototype_start_up_page


**Figure 1:** Screenshot of prototype when the oxygen concentrator is turned off and there is no noise.

In Figure 2 the concentrator has now been turned on and it is clear that all three readings have risen in value. However, because the mean microphone output is below the required threshold, the screen is still red which incorrectly suggests that the concentrator is still off.

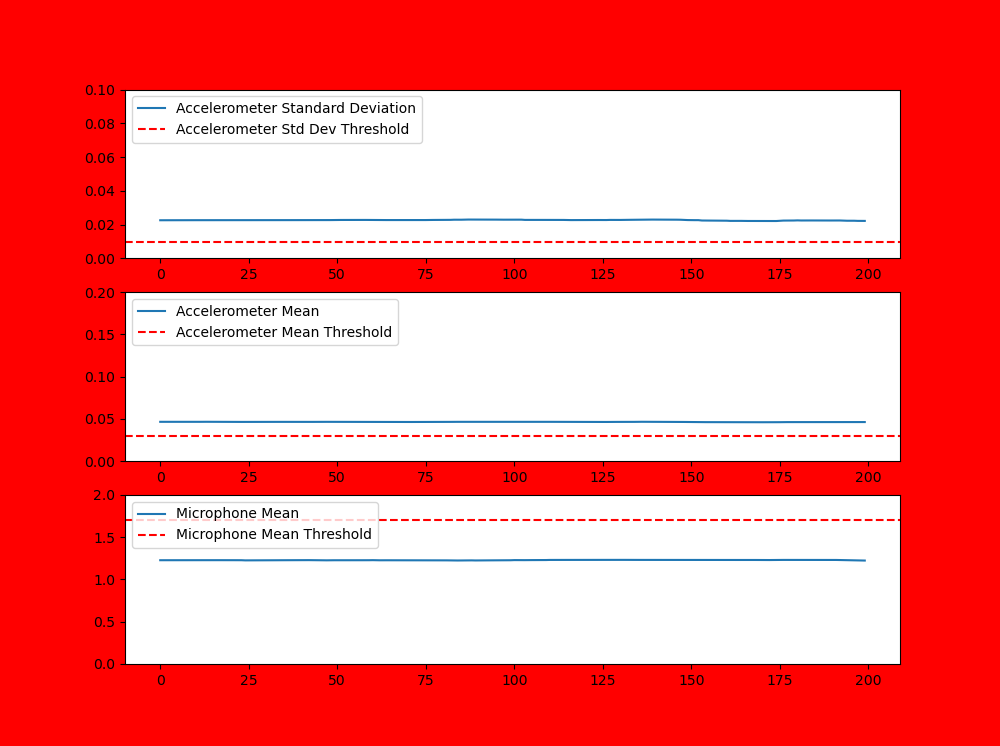
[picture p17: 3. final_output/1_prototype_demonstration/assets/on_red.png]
wrongly set thresholds


**Figure 2:** Screenshot of prototype when the oxygen concentrator is turned on, but the thresholds have not been calibrated.

In Figure 3 it shows an orange screen, which means the button has been pressed on the monitoring device, and threshold calibration is taking place. This calibration should be performed when the concentrator is turned on and only in the presence of quiet background noise. The calibration runs for 10 seconds and then adjusts the thresholds based off the incoming data that it has received.

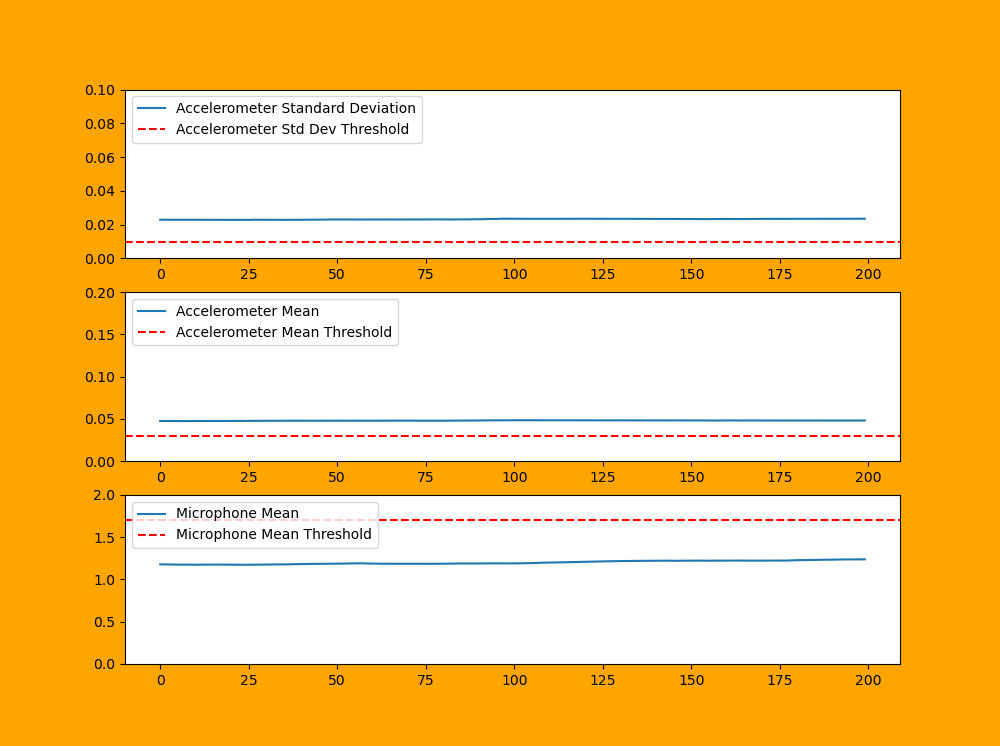
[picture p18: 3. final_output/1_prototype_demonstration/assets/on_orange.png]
threshold adjustment


**Figure 3:** Screenshot of prototype when the oxygen concentrator is turned on and the thresholds are being calibrated.

Figure 4 shows a screenshot of the output once calibration has been completed. The thresholds have been adjusted to match the specifications of the particular concentrator that it is monitoring. The screen has now turned green, which means the device is correctly monitoring the fact that the concentrator is on and running.

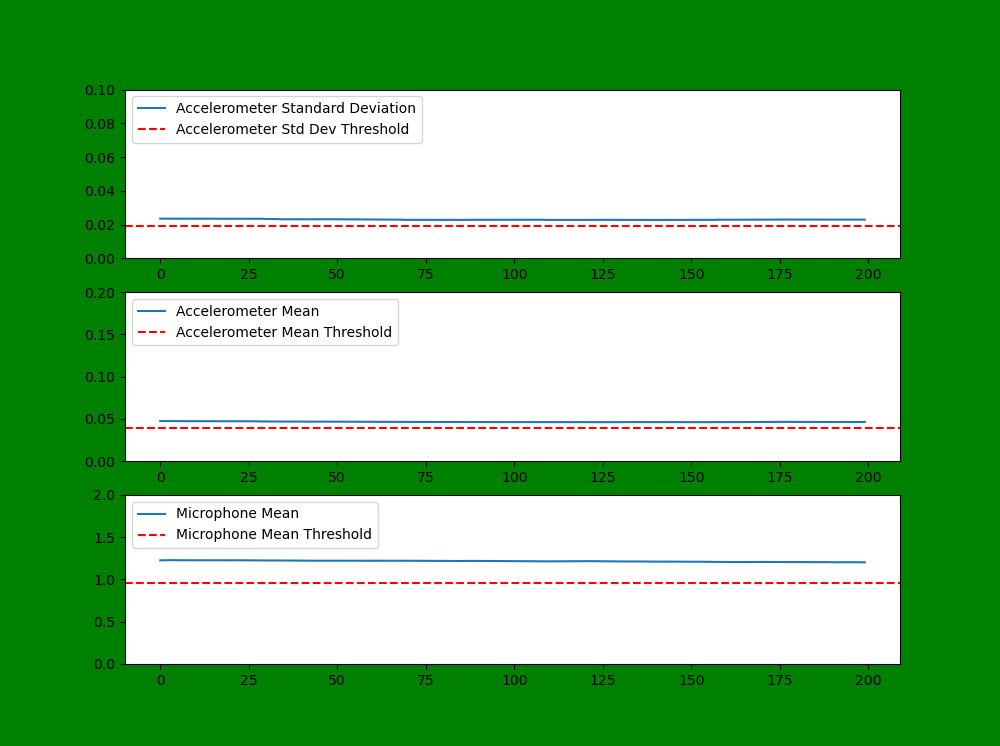
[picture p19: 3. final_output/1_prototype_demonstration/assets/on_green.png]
working thresholds


**Figure 4:** Screenshot of prototype when the oxygen concentrator is turned on and the thresholds have been correctly set.

Finally, Figure 5 shows an example of one of the worst-case scenario noise tests. The oxygen concentrator is turned off and has been left on uneven ground. As well as this, a second much more powerful concentrator has been turned on and left running directly next to the concentrator that the device is trying to monitor. Whilst the magnitude threshold has been met, both the noise and standard deviation measures have remained below the thresholds, and so the screen has remained red.

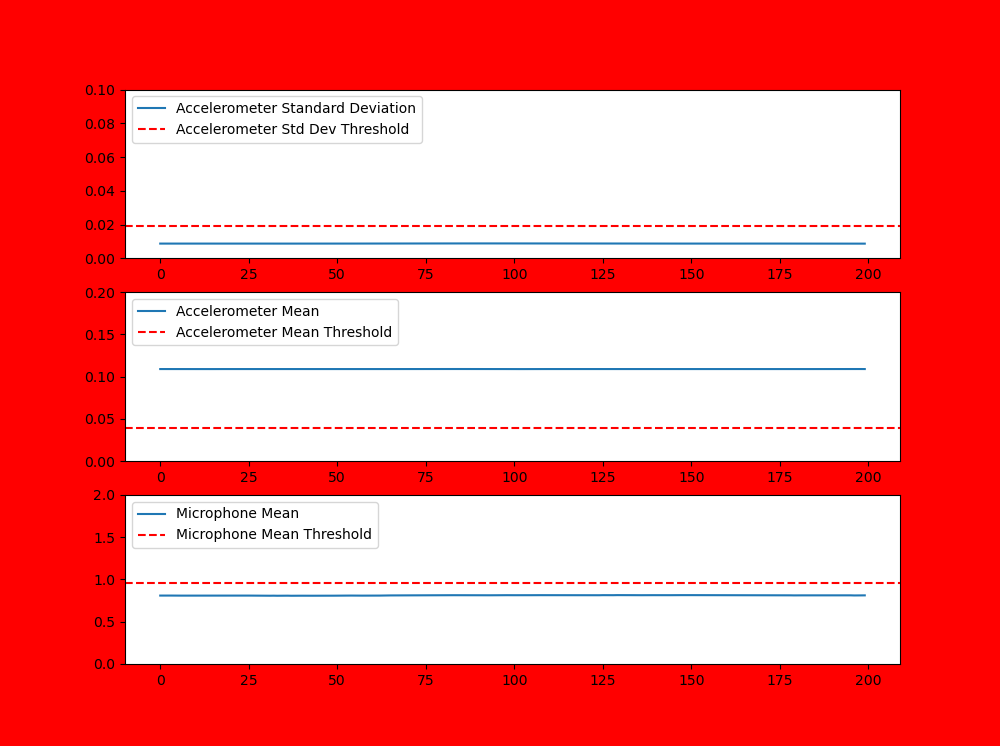
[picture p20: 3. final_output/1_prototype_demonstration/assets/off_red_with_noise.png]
dealing with noise


**Figure 5:** Screenshot of prototype when the oxygen concentrator is turned off and the thresholds have been correctly set, but the concentrator has been left on uneven ground and there is noise from another nearby concentrator.

Throughout all of the various tests that have been performed (as can be found in the `5_testing_results` folder), this threshold system proved to be robust against most sources of external noise that we were able to simulate in the Dyson Centre workshop.

It is important, however, that further tests are performed under the conditions that this device would actually be used, in order to see what level of precision and reliability it can achieve.

Further considerations for both the refinement and improvement of this prototype can be found in the `4_further_considerations` folder.

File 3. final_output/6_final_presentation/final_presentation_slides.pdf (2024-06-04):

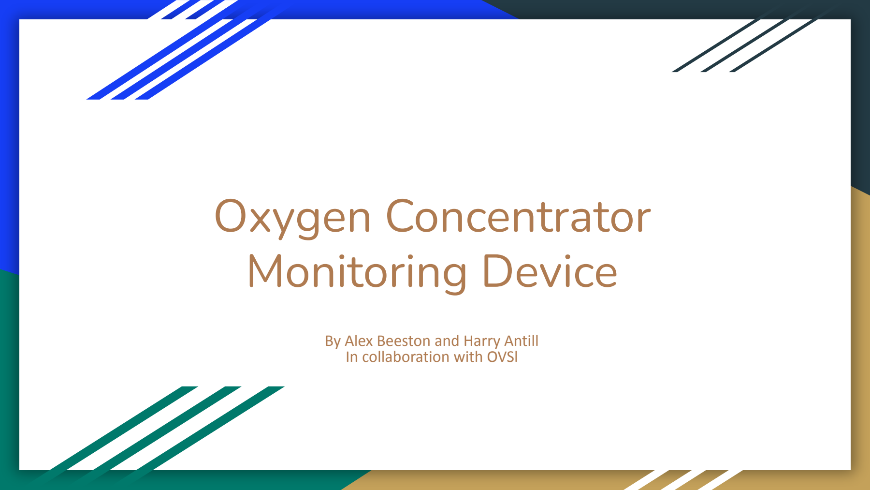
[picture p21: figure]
Oxygen Concentrator Monitoring Device; By Alex Beeston and Harry Antill In collaboration with OVSl

# The Problem

- Pneumonia kills more children every year than any other infectious disease.
- UNICEF believe that almost all of these deaths are preventable.

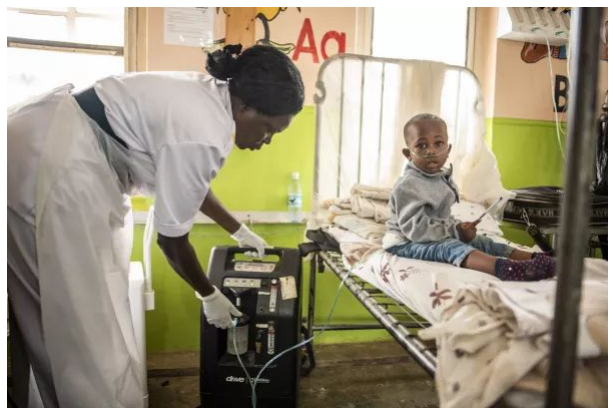
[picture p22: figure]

https://www.unicef.org/innovation/resilient-oxygen-concentrators

- Having access to robust medical
oxygen supplies is key.
- However, oxygen concentrators often fail to operate reliably in regions where pneumonia is most prevalent.
- Also, Ministries of Health have very little data relating to the usage of their concentrators.

# Our Partner:

- OVSI aim to ensure every individual has reliable access to essential medical oxygen.
- One of their four innovation domains is to develop a non-intrusive monitoring device.
- Our project looks at early stage testing of potential monitoring solutions.

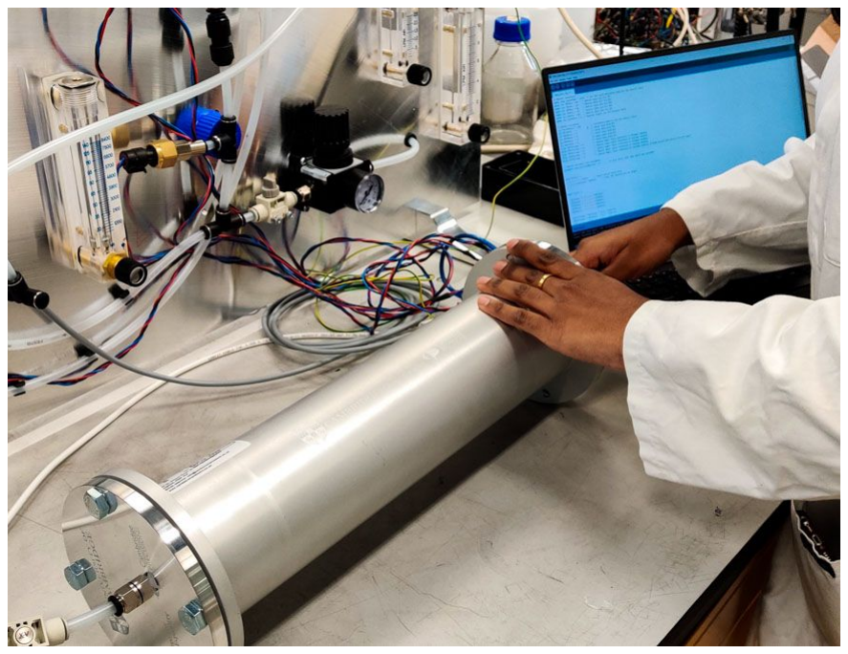
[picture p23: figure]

https://www.ovsi.org/

# Our Solution

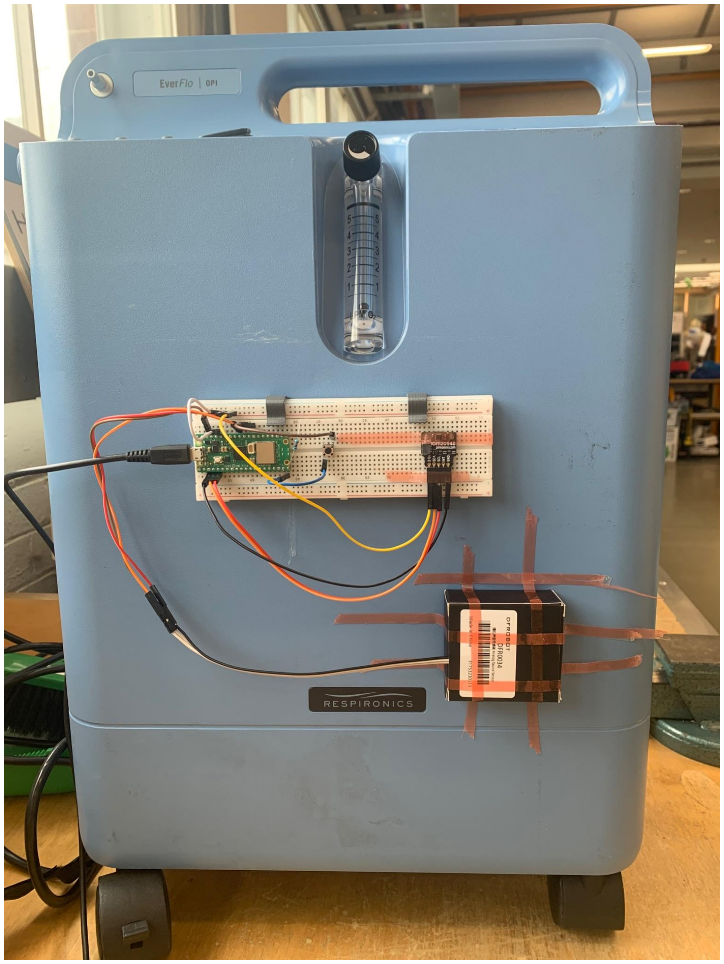
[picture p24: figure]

- Dual sensor monitoring device that accurately reports the operational status.
- Syncing function allows for long-term accuracy and compatibility with all oxygen concentrators.
- Scope to perform predictive maintenance.

# Sensors and Circuitry

- Breadboard setup for reading sensor outputs


- Key Components:
- Raspberry Pi Pico WH
- Accelerometer
- Microphone

# Hardware


- A solution for removing the effect of external noise on the microphone.
- A clip for mounting the sensors on the oxygen concentrator’s outer casing.


# Prototype Demonstration


- The photo on the right shows the
output of the monitoring device.
- In this test the monitoring device had just been placed on a new concentrator.
- The concentrator was on and running.
- However, the red screen shows it was incorrectly monitoring the concentrator as ‘off’.

# The Prototype Interface


- A simple button press puts the
device into calibration mode.
- This is shown by the orange screen.
- Calibration takes 10 seconds to perform.

# The Prototype Interface


- Calibration is now complete and the thresholds have been adjusted.
- The device is now correctly determining the concentrator as ‘on’.
- This is shown by the green display.
- When the concentrator is now turned off, the signals drop and the screen turns red.

# The Results

- When the concentrator was turned on, the device correctly displayed this 100% of the time during testing.
- When testing the robustness of the device against noise, the device proved accurate in all situations apart from when the concentrator was being wheeled around.
- Future work will involve adding machine learning algorithms and a GPS to eliminate this problem.

# Sustainable Development and Inclusive Innovation


- Our project aligns well with the United Nations’ Sustainable Development Goals:
- SDG 3: Good Health and Well-being
- SDG 9: Industry, Innovation, and Infrastructure
- Our project also follows the principles of Inclusive Innovation:
- Impact focused
- Enhances agency
- Responds to a genuine need
Image from:
https://international-partnerships.ec.europa.eu/policies/sustainable-development-goals_en

# What’s next?


- We have documented our work in a reproducible format allowing OVSI to understand the prototype and carry it forwards.
- OVSI may choose to pursue the recommendations we have given for future work.
- After many iterations and field studies, a refined version of the monitoring device will be implemented in LEDCs.

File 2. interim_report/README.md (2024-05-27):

# Interim Report

The file `interim_report.md` demonstrates the progress of the project roughly two and a half weeks into the timeline. It looks at the testing, results and prototype that had been developed up to the date of the report. It assesses how the work completed aligns with the original project proposal, and the different challenges and solutions that have been faced. The report also updates the project management timeline and presents a plan for completion.

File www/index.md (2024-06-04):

---
title: Home
---
# **Becoming Part of the Solution to Pneumonia**

#### **The Problem**

"Pneumonia kills more children than any other infectious disease, claiming the lives of over 700,000 children under five every year... almost all of these deaths are preventable" - UNICEF [2024]. It has been shown that in countries with robust oxygen systems, hospital-based pneumonia deaths can be reduced by half. However, due to the harsh operating environment in Sub-Saharan Africa and South East Asia where pneumonia is most prevalent, these oxygen concentrators often fail to operate reliably.

#### **Our Partner OVSI**

The Oxygen and Ventilator System Initiative (OVSI) "wants to ensure every individual has reliable and equitable access to essential medical oxygen". One of their key innovation domains is in developing a remote monitoring system that can integrate with all types of existing concentrators to track their usage and schedule predictive maintenance. 

Hopsital Picture UNICEF

https://www.unicef.org/innovation/resilient-oxygen-concentrators 

#### **How We Fit In**

Our aim was to assess the feasibility of a non-intrusive monitoring device for oxygen concentrators. This involved experimenting with different sensors such as microphones and accelerometers to provide useful insight for OVSI on the most promising approaches to collecting usage data on oxygen concentrators. See [Our Prototype](about.md) page for more information.

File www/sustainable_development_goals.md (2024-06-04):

---
title: Sustainable Development
---

The United Nations' sustainable development goals (SDGs) are ‘a call to action to end poverty and inequality, protect the planet, and ensure that all people enjoy health, justice and prosperity’ (World Health Organisation 2021). These goals provide a framework for governments, firms, and individuals to work towards achieving a more sustainable and equitable future. The below points show how our project aligns with the SDGs to promote a better and more sustainable future.

#### **SDG 3: Good Health and Well-being**

**Target 3.2:** End preventable deaths of newborns and children under 5 years of age.  

As discussed in the project overview page, pneumonia is responsible for hundreds of thousands of deaths of children under the age of 5 every year. By helping in the early stage design of an effective oxygen concentrator monitoring system it is hoped that this project can directly contribute to tackling this issue by improving the quality of healthcare provided to children suffering from pneumonia.

**Target 3.8:** Achieve universal health coverage, including access to quality essential health-care services and access to safe, effective, quality, and affordable essential medicines and vaccines for all.  

The monitoring device supports the aim of universal health coverage by ensuring that oxygen concentrators (a crucial medical resource in the treatment of pneumonia) are well maintained and consistently operational, thus enhancing the quality of healthcare services in low-resource settings.

#### **SDG 9: Industry, Innovation, and Infrastructure**

**Target 9.1:** Develop quality, reliable, sustainable, and resilient infrastructure, including regional and transborder infrastructure, to support economic development and human well-being, with a focus on affordable and equitable access for all.  

By designing a reliable monitoring device for oxygen concentrators, the project contributes to building resilient healthcare infrastructure in developing regions, in order to ensure that essential medical equipment remains functional and effective. It should help to reduce the downtime of oxygen concentrators that occurs during repairs, as well as extending the useful lifetime the concentrators.

#### **SDG 12: Responsible Consumption and Production**

**Target 12.5:** Substantially reduce waste generation through prevention, reduction, recycling, and reuse.  

This project begun the initial design and development of a monitoring device which ultimately looks to incorporate degradation monitoring functionality into the system. This means that as the concentrators condition begins to worsen, the monitoring device can recognise this through the signals it is receiving and therefore help to schedule maintenance before the concentrator breaks down. This focus on preventive maintenance and early fault detection for oxygen concentrators helps extend their lifespan, reducing medical equipment waste and promoting sustainable use of resources.

#### **SDG 17: Partnerships for the Goals**

**Target 17.6:** Enhance North-South, South-South, and triangular regional and international cooperation on and access to science, technology, and innovation and enhance knowledge sharing on mutually agreed terms.  

The project encourages collaboration between various stakeholders, including Ministries of Health, biomedical engineers, and international organizations. This project had a strong focus on knowledge sharing and implementing inclusive innovation in the development of new healthcare technologies.

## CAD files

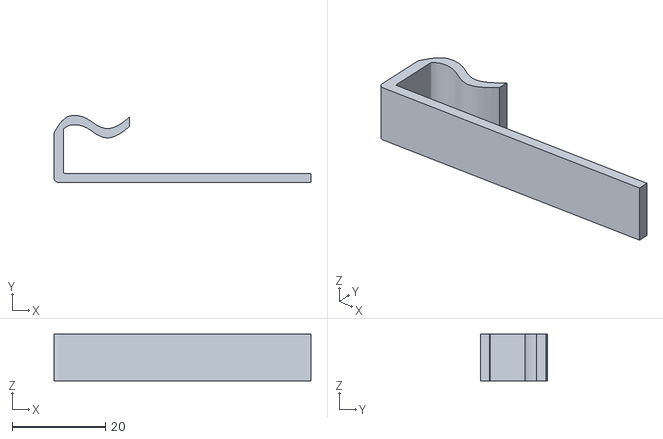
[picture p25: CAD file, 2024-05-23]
3. final_output/2_hardware_and_circuitry/Assets/clip.STL
55.0 x 14.4 x 10.0

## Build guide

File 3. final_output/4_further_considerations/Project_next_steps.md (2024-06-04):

# Further considerations

In this 4 week project we made a triple threshold monitoring device for oxygen concetrators that reliably indicated if the concentrator was being currently running, when tested under a range of simulated interference conditions. In order to take it further, a list of potential considerations for Ben Moore and OVSI are given below.

### Additional functions

| Function                     | Explanation                                                                                                                                                                 |
|------------------------------|-----------------------------------------------------------------------------------------------------------------------------------------------------------------------------|
| Microphone Housing           | Create more sophisticated housing for the microphone sensor to isolate sound from the concentrator and make the device more robust to external noise.                        |
| Accelerometer Housing        | Improved housing to reduce vibration damping through the attachment method. Also test to find the optimum location for the accelerometer on the concentrator casing to receive vibrations. |
| Degradation Monitoring       | Use machine learning algorithms to adjust thresholds over time as the output changes due to degradation. A very large data set would be required to allow this to be extended to include predictive maintenance. |
| Non-Orientation Specific     | Use the inbuilt gyros to eliminate the gravity component so orientation of the accelerometer is not important. This is preferable to manually zeroing the readings when there is no noise present.               |
| Visual Indicator             | Incorporating an LED on the device to give visual reading on the device will allow for immediate recognition of device failure or malfunction.                               |
| Specialised Microcontroller  | Design a microcontroller to perform the specific required function. This makes the device cheaper and smaller when mass produced.                                          |
| Fourier Analysis of Vibrations | Determine frequencies of vibrations through a Fourier analysis. This could give unique signatures for concentrators and then be used to detect degradation.                   |
| GPS tracking                 | Additional GPS tracker in device will provide additional useful information for Ministries of Health, as well as providing an extra threshold for the monitoring device to prevent transportation from being confused with use. |
| Data handling and storage                 | Determine how much of the processing will be done on the device, and how it will store any data which then needs to be transferred. |

### Additional contextual testing

| Test                    | Explanation                                                                                                                           |
|-------------------------|---------------------------------------------------------------------------------------------------------------------------------------|
| Hospital Test           | There may be interferences that we have not anticipated, so testing the device in a similar environment will be useful.                             |
| Environmental conditions| Test for high heat and humidity to see impact on function of concentrator and device respectively.                                     |
| Context                 | Usability study with doctors to find the level of interaction with the device they are willing to have.                                |

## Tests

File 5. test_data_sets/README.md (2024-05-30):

# Test Data Documentation

The `accelerometer_tests` folder contains all the .xlsx files which relate to the testing of the accelerometer.

The `microphone_tests` folder contains all the .xlsx files which relate to the testing of the microphone.

The `combined_sensor_tests` folder contains all the .xlsx files which relate to the testing of the device when both the accelerometer and the microphone were attached.

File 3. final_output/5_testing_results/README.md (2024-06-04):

# Sensor Testing

Various tests were performed to assess the usefulness of an accelerometer and microphone in measuring the usage of an oxygen concentrator.

The testing was performed in the following order:
- Accelerometer testing
- Microphone testing
- Combined testing with both sensors

The raw data from all of these tests can be found in `5. test_data_sets`.

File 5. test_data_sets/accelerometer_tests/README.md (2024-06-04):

# Accelerometer Test Data

The `.xlsx` files in this folder contain all of the data that was collected during the tests that were performed for the interim report, and relate to the testing of the accelerometer. The file names are constructed with the following naming convention:
- The first part of the name shows the concentrator that the accelerometer was attached to
- The second part shows whether or not the concentrator that the accelerometer was attached to was turned on or off
- The rest of the name relates to the particular test being performed

Here is an explanation of each test:
- 'No noise' means that the output was recorded in quiet conditions
- 'Touching' means that another concentrator was turned on and placed in direct contact with the concentrator being measured
- '10cm away' means that another concentrator was turned on and placed 10cm away from the concentrator being measured
- 'Trolley and walking' explains the sources of noise that were present during testing
- 'Uneven ground' shows the test results when the concentrator was left on uneven ground

Further information can be found in `3. final_output/5_testing_results`.

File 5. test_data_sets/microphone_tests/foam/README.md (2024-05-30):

# Microphone with Insulation Test Data

All tests were performed with the microphone attached to the blue Everflo oxygen concentrator.
The tests performed were as follows:
- `blue_on_foam` recording the output when the blue concentrator was turned on with no noise in the background
- `no_noise_foam` recording the output when the blue concentrator was turned off and with no noise in the background
- `random_noise_foam` recording the output when there was noise from walking, talking, clapping etc
- `black_on_near_blue_foam` recording the output when the black concentrator was on and running roughly 10cm from the blue concentrator

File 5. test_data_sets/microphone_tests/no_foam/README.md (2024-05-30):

# Microphone Without Insulation - Test Data

All tests were performed with the microphone attached to the blue Everflo oxygen concentrator.
The tests performed were as follows:
- `blue_on` recording the output when the blue concentrator was turned on with no noise in the background
- `no_noise` recording the output when the blue concentrator was turned off and with no noise in the background
- `random_noise` recording the output when there was noise from walking, talking, clapping etc
- `black_on_near_blue` recording the output when the black concentrator was on and running roughly 10cm from the blue concentrator

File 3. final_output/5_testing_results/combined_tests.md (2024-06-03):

# Combined Sensor Testing

Once the testing of the individual sensors had been completed as shown in `accelerometer_tests.md` and `microphone_tests.md`, we combined the sensors to create one complete circuit as shown in `hardware_and_circuitry.md`.

We then performed further testing to see how we could use the sensors to determine whether or not the concentrator was running. The three pieces information that were being calculated were:
- The 10s rolling mean of the accelerometer magnitude
- The 10s rolling standard deviation of the accelerometer magnitude
- The 10s rolling mean of the microphone reading

The accelerometer magnitude was being measured in "g" and the microphone output was being measured as a % of the maximum value it was capable of reading.

We then performed the following tests:
- Concentrator on
- Concentrator off and no noise
- Concentrator off and being rolled around
- Concentrator off and being carried around
- Concentrator off and noise from walking, talking and other random Dyson Centre workshop noise

The data from the tests that were run over a 60 second time period were plotted on a 3D scatter plot as shown in Figure 1 below.

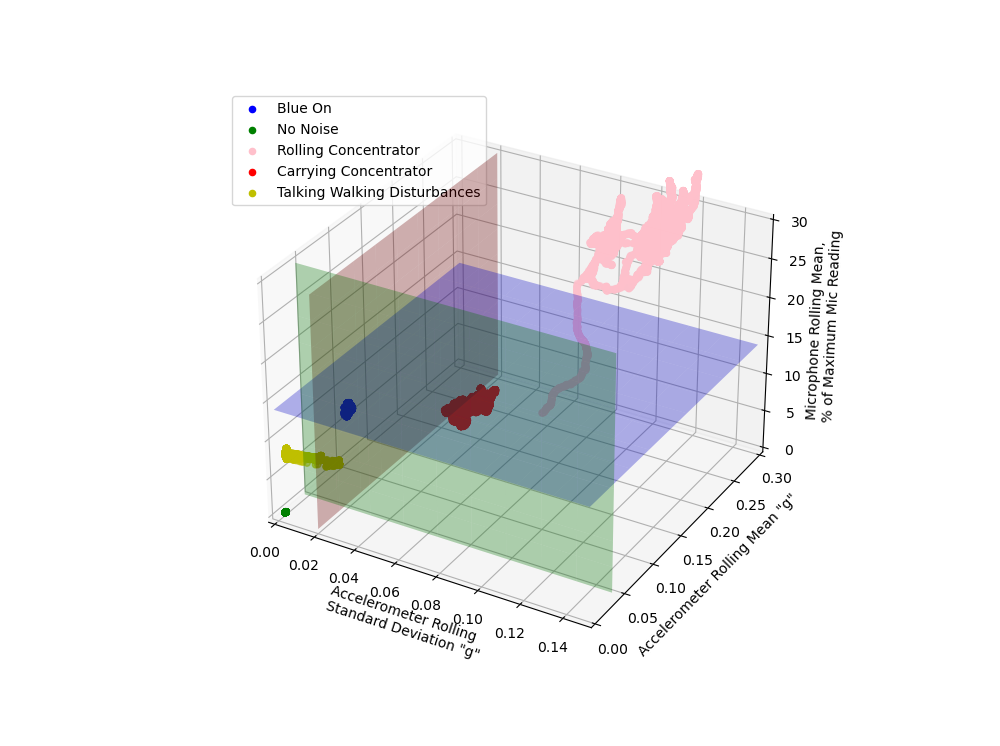
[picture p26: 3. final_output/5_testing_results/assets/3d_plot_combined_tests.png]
3d space of sensor output


**Figure 1:** 3D scatter plot showing the datapoints from the various test scenarios.

Figure 1 itself cannot be used to interpret the data as it shows a 3d space on a 2d screen. However, it should help to understand the following discussion points from testing. In order to traverse the 3d space the data is included in the `test_data/combined_sensor_tests` folder and the code to run it is included in the `code/combined_sensors_code/3d_plot_past_data.py` file.

Once all of the data was plotted in the 3d space it was possible to investigate how the different sources of noise would occupy the space. It became quickly apparent that it was possible to separate all of the noise sources from the 'on' case by setting a threshold for each of the three axes, which all had to be met at the same time to show that the concentrator was running. These thresholds have been plotted on the scatter plot as planes.

The only noise case that violated all of these thresholds at once was rolling the concentrator around on a rough floor. However, we anticipate this will cause only a slight discrepancy in use data due to the length scales of each case (the concentrator will be running for hours each day but only moved for a few minutes). This should be confirmed with further testing. Methods to investigate this effect and potentially eliminate it are discussed in the `further_considerations.md` document.

Excluding the effect of rolling the concentrator around, the threshold system was 100% accurate over the duration of all tests performed throughout this project. However, further testing over longer duration timescales should be performed to verify this level of accuracy.

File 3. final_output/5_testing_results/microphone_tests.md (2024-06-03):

# Microphone Testing

In order to test the robustness of the microphone sensor we recorded the output over a range of different tests:
- measuring the output when the sensor is on a concentrator and the concentrator is running
- measuring the output when the sensor is on a concentrator and the concentrator is turned off
- measuring the output when the concentrator is turned off, but another concentrator is running 10cm away
- measuring the output when the concentrator is turned off but there is noise from talking, walking, knocks to the concentrator and random noise from the Dyson Centre workshop

Having performed the accelerometer testing, it was clear from the large magnitude of vibrations and high noise level from the black concentrator, that it would be the blue concentrator that was the limiting case. Hence, for the microphone testing, all of the tests were performed solely on the blue concentrator.

Figure 1 below shows each the four tests above run under two different conditions:
- the microphone attached to the concentrator with no external casing
- the microphone attached to the concentrator when surrounded by a cardboard box filled with sponge foam

The set-up and explanation of the sponge foam as noise isolation can be found in the `hardware_and_circuitry.md` file.

The y-axis on Figure 1 is measured as a percentage of the maximum reading that the microphone is capable of receiving. The size of the bars themselves represent the mean noise level over the duration of the 60 second tests.

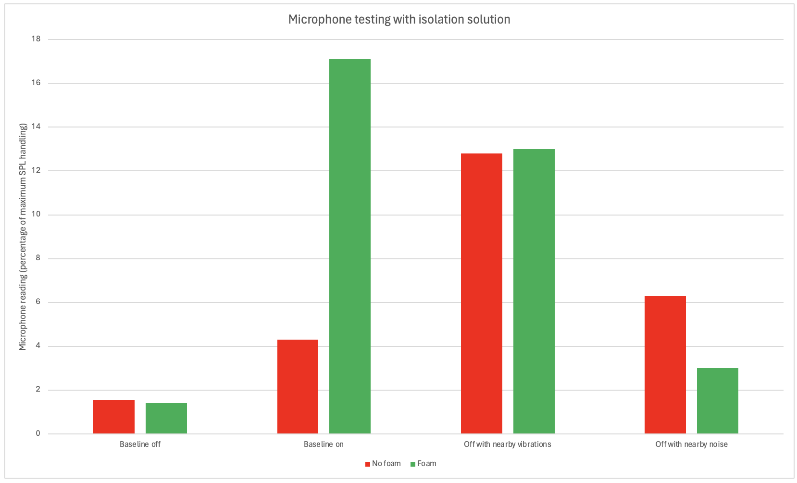
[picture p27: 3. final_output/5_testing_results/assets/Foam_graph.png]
bar chart of microphone testing


**Figure 1:** Bar chart from the microphone testing performed on the blue concentrator.

It is clear from Figure 1 that without any surrounding casing to eliminate the effects of external noise, that the microphone would not provide a useful measure of whether or not the concentrator is running. However, by surrounding the sensor with foam (apart from on the side of the sensor that was in direct contact with the oxygen concentrator), the largest noise readings were then found for the case where the concentrator was running. Following this testing, it was then determined that the microphone would be incorporated into the final prototype.

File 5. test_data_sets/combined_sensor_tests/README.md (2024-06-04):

These are the datasets that were recorded during the testing described in `3. final_output/5_testing_results`. Refer to this page for descriptions of each test.

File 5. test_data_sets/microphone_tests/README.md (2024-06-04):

# Microphone Test Data

The `.xlsx` files in this folder contain all of the data that was collected during the tests that relate to the testing of the microphone. 
The `no_foam` folder contains the results from the microphone tests when the microphone was simply stuck to the side of the concentrator. 
The `foam` folder contains the results from the microphone tests when it was stuck to the side of the concentrator and insulated with foam to eliminate external noise as best as possible with a rapid prototype.

Further information can be found in `3. final_output/5_testing_results`.

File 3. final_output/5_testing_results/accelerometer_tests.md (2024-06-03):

# Accelerometer Testing

In order to test the robustness of the accelerometer sensor we recorded the accelerometer output over a range of different tests:
- measuring the output when the sensor is on a concentrator and the concentrator is running
- measuring the output when the sensor is on a concentrator and the concentrator is turned off
- measuring the output when the concentrator is turned off, but another concentrator is running and making direct contact
- measuring the output when the concentrator is turned off, but another concentrator is running 10cm away
- measuring the output when the concentrator is turned off but there is external noise from walking, talking, rolling a trolley and other noises from the Dyson Centre workshop
- measuring the output when the concentrator is turned off, but it has been left on an uneven slope

Each of these tests were performed firstly with the accelerometer on the black oxygen concentrator and using the blue concentrator to make noise in the other tests. Then they were performed with the accelerometer on the blue concentrator and the black concentrator was used to make noise. The exact models of the two concentrators can be found in the `hardware_and_circuitry.md` file.

In order to present the results, a 1000 reading (i.e. roughly 10 seconds) rolling mean and standard deviation were recorded throughout the duration of the 120 second test. In order to assess how well these measures can determine whether or not the concentrator is turned on or off, the charts below show the smallest readings of mean and standard deviation that were recorded over the duration of the test for the 'concentrator on' case, and then the largest readings of mean and standard deviation for the other noisy test cases.

It is clear from Figure 1 that the magnitude of the vibrations of the black concentrator are large enough to make it very robust against other noise. In all cases the mean and standard deviation during the 'on' case were significantly larger than any of the other test cases, and as such it is simple for the sensor to use these measures to determine when the concentrator is on or off.

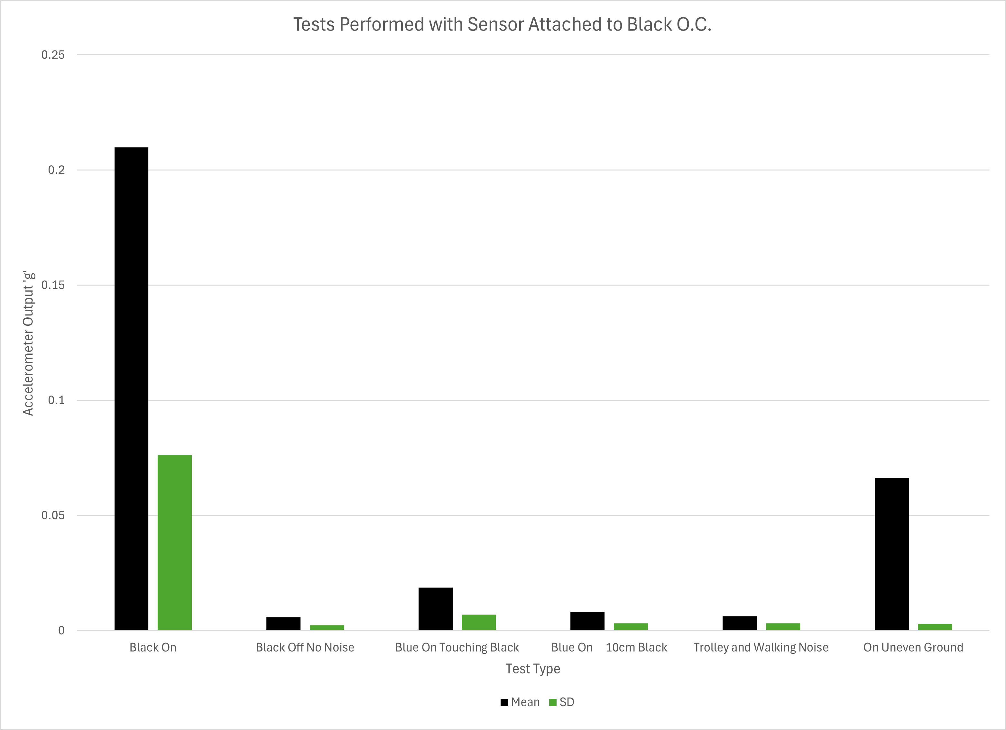
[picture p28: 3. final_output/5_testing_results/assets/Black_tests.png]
bar chart of black oc tests


**Figure 1:** Bar chart from the testing performed on the black concentrator.

However, the Figure 2 below tells a different story. The blue EverFlo concentrator is significantly more quiet - 43dB rather than 69dB for the black one. The most common concentrators used in the target market are 40-50dB, so this is more indicative of the results we would expect to see during service. Here the results show that the mean and standard deviation for the noise test cases can be of a similar or greater magnitude than the baseline-on case. This makes detection more difficult. Having the powerful black concentrator turned on next to the blue concentrator gives readings of comparable value as when the blue concentrator is running, and so this could give false readings. Furthermore, uneven ground gives large readings for the magnitude, so any unexpected placement of the concentrator could give false readings. Also, the standard deviation for the concentrator off and no noise test was much larger than expected, and after further analysis this was due to just a few larger readings over the course of the test, which shows the ability of short knocks or impacts to the concentrator to spike the standard deviation reading.

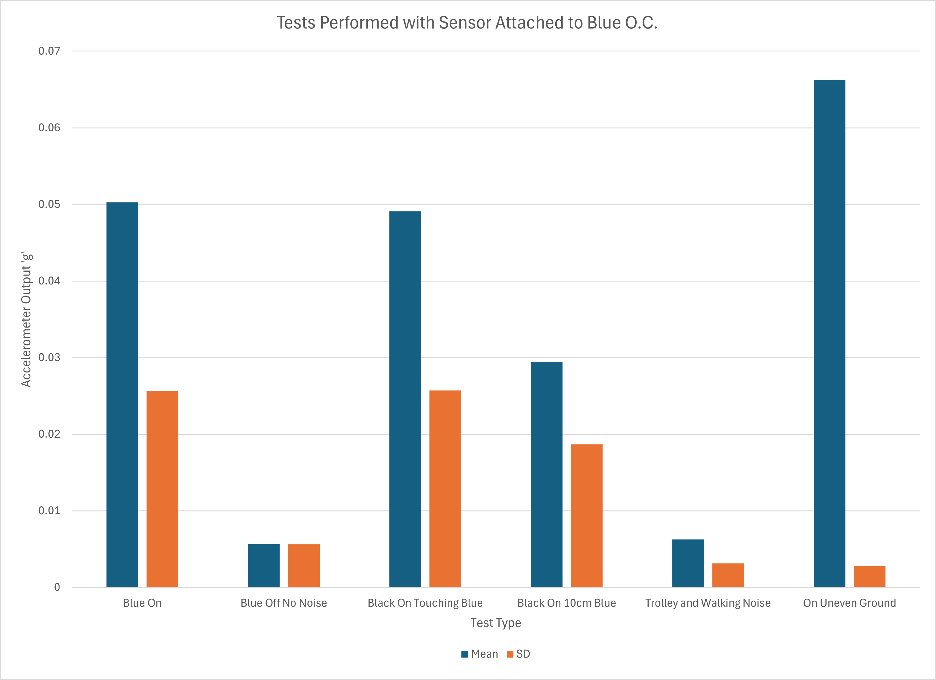
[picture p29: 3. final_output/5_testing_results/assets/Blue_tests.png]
bar chart of blue oc tests


**Figure 2:** Bar chart from the testing performed on the blue concentrator.  

Figure 3 shows the readings from the tests performed on the two oxygen concentrators placed next to each other for easy comparison. This shows that any strongly vibrating machinery placed nearby to the blue concentrator could result in false readings, whereas for the black concentrator it is much easier to differentiate the on and off state.

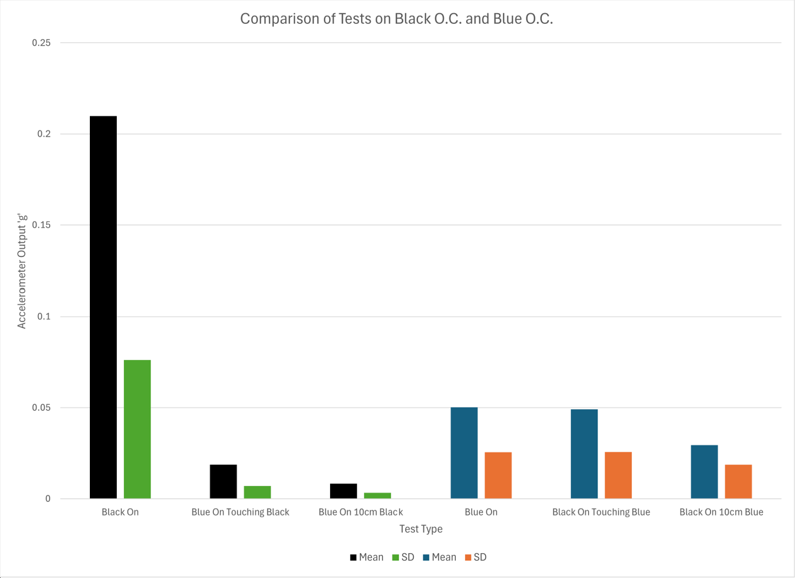
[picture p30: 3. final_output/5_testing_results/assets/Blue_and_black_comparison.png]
comparison of blue and black tests


**Figure 3:** Bar chart comparing the data between the black and blue concentrator tests.

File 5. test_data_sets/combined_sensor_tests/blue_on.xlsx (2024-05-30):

Mean Magnitude | Standard Deviation | Microphone Output
0.046332 | 0.0231825317 | 1.2959
0.046339 | 0.02317805167 | 1.2953
0.046288 | 0.02314240817 | 1.29503
0.046293 | 0.02314439783 | 1.29492
0.046326 | 0.02316462225 | 1.29508
0.046294 | 0.0231843819 | 1.29493
0.046211 | 0.02306145006 | 1.29423
0.04619 | 0.02303293077 | 1.29339
0.04615 | 0.0230175911 | 1.29325
0.046115 | 0.02303983019 | 1.29395
0.046074 | 0.02302130587 | 1.29397
0.04603 | 0.02299845864 | 1.29271
0.046045 | 0.02298897508 | 1.29236
0.046036 | 0.02299153549 | 1.29324
0.046001 | 0.02299080249 | 1.29306
0.045994 | 0.02299125843 | 1.29284
0.046034 | 0.02297208837 | 1.29215
0.046022 | 0.02298150378 | 1.29272
0.045963 | 0.02297249727 | 1.29212
0.045949 | 0.0229858739 | 1.29225
0.045921 | 0.02298335831 | 1.29184
0.045916 | 0.02298736488 | 1.29211
0.045855 | 0.022921954 | 1.29188
0.04583 | 0.02294957734 | 1.29097
0.045818 | 0.02294634777 | 1.29055
0.045811 | 0.02295162911 | 1.29114
0.045791 | 0.02294361173 | 1.29142
0.045809 | 0.02293827629 | 1.29138
0.045806 | 0.02293792414 | 1.29109
0.045848 | 0.02295288426 | 1.28997
0.045829 | 0.02292500292 | 1.28938
0.045812 | 0.0229274651 | 1.28889
0.045832 | 0.02293982947 | 1.28847
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

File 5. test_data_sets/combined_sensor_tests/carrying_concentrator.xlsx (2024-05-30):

Mean Magnitude | Standard Deviation | Microphone Output
0.146697 | 0.04596271523 | 0.54091
0.1468 | 0.04596888078 | 0.54075
0.146864 | 0.04596911467 | 0.54037
0.146929 | 0.04595582617 | 0.54057
0.146994 | 0.0459452714 | 0.54019
0.14705 | 0.04593793095 | 0.5401
0.147087 | 0.0459229728 | 0.54014
0.147088 | 0.04592274225 | 0.5399
0.147076 | 0.04592616056 | 0.53972
0.147048 | 0.0459316851 | 0.53957
0.147048 | 0.0459316851 | 0.53943
0.147062 | 0.04593624012 | 0.53873
0.147102 | 0.04595619214 | 0.53807
0.147145 | 0.04598180048 | 0.53729
0.14718 | 0.04600032174 | 0.53709
0.147207 | 0.04601634656 | 0.53712
0.147224 | 0.04602162344 | 0.53698
0.147241 | 0.04602467728 | 0.53712
0.147255 | 0.04602490603 | 0.53733
0.147254 | 0.0460249876 | 0.53733
0.147249 | 0.04602517788 | 0.53748
0.147234 | 0.04602672315 | 0.53741
0.147239 | 0.04602588271 | 0.53733
0.147237 | 0.04602615377 | 0.53741
0.14724 | 0.04602538865 | 0.53714
0.147215 | 0.0460355599 | 0.53704
0.147178 | 0.04605701158 | 0.53708
0.147123 | 0.04609479223 | 0.53727
0.147067 | 0.04613376758 | 0.53754
0.147022 | 0.04616257701 | 0.53735
0.14699 | 0.04617713612 | 0.53724
0.146977 | 0.04617896135 | 0.53709
0.146967 | 0.04618112072 | 0.53697
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

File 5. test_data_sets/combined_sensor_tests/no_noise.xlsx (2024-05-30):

Mean Magnitude | Standard Deviation | Microphone Output
0.004599 | 0.001881541655 | 0.03157
0.004596 | 0.001881697106 | 0.03149
0.004593 | 0.001881847762 | 0.03149
0.004595 | 0.001881216362 | 0.0314
0.00459 | 0.00187880281 | 0.03141
0.004591 | 0.001878754641 | 0.03135
0.004595 | 0.001877491678 | 0.03147
0.004596 | 0.001876908096 | 0.03144
0.004598 | 0.001876271835 | 0.03151
0.004598 | 0.001876271835 | 0.03158
0.004596 | 0.001876908096 | 0.03156
0.004601 | 0.001873979456 | 0.03154
0.004597 | 0.001877389411 | 0.03154
0.004598 | 0.00187787007 | 0.03165
0.004598 | 0.00187787007 | 0.03172
0.004593 | 0.00187546021 | 0.03176
0.00459 | 0.00187880281 | 0.03169
0.004592 | 0.001880302103 | 0.03169
0.004596 | 0.001879038052 | 0.03164
0.004589 | 0.001871918535 | 0.03157
0.004592 | 0.001873375563 | 0.03168
0.004591 | 0.001873958111 | 0.0317
0.004594 | 0.001878606931 | 0.03185
0.004595 | 0.001879088875 | 0.03184
0.004592 | 0.001879238144 | 0.03181
0.004592 | 0.001879238144 | 0.03173
0.00459 | 0.001879867017 | 0.03173
0.004588 | 0.001877300189 | 0.03172
0.004589 | 0.001876720278 | 0.03172
0.00459 | 0.001876139654 | 0.03174
0.00459 | 0.001876139654 | 0.03183
0.004587 | 0.001874681573 | 0.03174
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

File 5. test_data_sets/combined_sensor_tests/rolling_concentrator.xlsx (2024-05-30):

Mean Magnitude | Standard Deviation | Microphone Output
0.082588 | 0.1048207911 | 1.62258
0.082656 | 0.104795733 | 1.62471
0.083016 | 0.105159801 | 1.62535
0.083131 | 0.1051416751 | 1.62758
0.083477 | 0.1054561211 | 1.63045
0.083618 | 0.105448035 | 1.63263
0.08376 | 0.1054538401 | 1.63456
0.083852 | 0.1054409223 | 1.63661
0.083939 | 0.105425743 | 1.6378
0.084212 | 0.1055950238 | 1.64079
0.084306 | 0.1055796589 | 1.64567
0.084537 | 0.1056694972 | 1.64819
0.084663 | 0.1056508941 | 1.6506
0.084864 | 0.1056922396 | 1.65287
0.085122 | 0.1058386183 | 1.65567
0.085307 | 0.1058758176 | 1.65678
0.085432 | 0.1058594416 | 1.65928
0.085546 | 0.1058395289 | 1.66155
0.085733 | 0.1058622488 | 1.66321
0.085957 | 0.1059556377 | 1.66608
0.086056 | 0.1059374101 | 1.66955
0.086197 | 0.1059232656 | 1.67103
0.086342 | 0.1059126293 | 1.67241
0.08654 | 0.1059604002 | 1.67465
0.086617 | 0.1059327254 | 1.67712
0.08702 | 0.1064059942 | 1.67862
0.08715 | 0.1063826748 | 1.68083
0.087341 | 0.106415444 | 1.68266
0.087638 | 0.1066078747 | 1.68719
0.087829 | 0.1066486557 | 1.68866
0.088065 | 0.1067394621 | 1.6908
0.088377 | 0.1069549011 | 1.69299
0.08856 | 0.1069737744 | 1.69438
0.088632 | 0.1069444275 | 1.69564
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

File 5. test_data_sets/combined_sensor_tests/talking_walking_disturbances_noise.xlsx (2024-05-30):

Mean Magnitude | Standard Deviation | Microphone Output
0.010403 | 0.01119940137 | 0.81265
0.010404 | 0.01119914211 | 0.81286
0.0104 | 0.01120107138 | 0.81341
0.010397 | 0.01120157984 | 0.8139
0.010392 | 0.01120376437 | 0.81444
0.010391 | 0.0112041117 | 0.81418
0.01039 | 0.01120445893 | 0.81452
0.010383 | 0.01120501276 | 0.81469
0.01038 | 0.01120524877 | 0.81535
0.010385 | 0.01120440873 | 0.8162
0.010376 | 0.01120511597 | 0.8161
0.010373 | 0.01120642097 | 0.8162
0.010368 | 0.01120725551 | 0.81655
0.010364 | 0.01120952738 | 0.81651
0.01036 | 0.01121072701 | 0.81646
0.010369 | 0.01120923008 | 0.81617
0.010366 | 0.01120972988 | 0.81688
0.010368 | 0.01120859385 | 0.81749
0.010371 | 0.01120729044 | 0.81738
0.010373 | 0.01120668867 | 0.81738
0.010378 | 0.01120674422 | 0.81748
0.010376 | 0.01120752533 | 0.81654
0.010373 | 0.01120883005 | 0.81559
0.010378 | 0.01120888558 | 0.81399
0.01037 | 0.01121057982 | 0.81207
0.010373 | 0.01120981137 | 0.8107
0.010372 | 0.01121033523 | 0.80926
0.010379 | 0.01121041297 | 0.80802
0.010378 | 0.01121084814 | 0.80678
0.01038 | 0.01120988849 | 0.80597
0.010379 | 0.01121014536 | 0.80537
0.010376 | 0.01121145058 | 0.80466
0.01037 | 0.01121218534 | 0.80415
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

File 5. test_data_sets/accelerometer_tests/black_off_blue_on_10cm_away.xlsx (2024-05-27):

RAW DATA |  |  |  |  | (scroll to 10s to view data) |  |  | (same as column FGH but sorted by value)
X (g) | Y (g) | Z (g) | Magnitude (g) | time (s) | 10s moving avg | 10s moving std | 10s moving var | 10s moving avg | 10s moving std | 10s moving var
0.002 | 0.004 | 0.002 | 0.005 | 0.01 |  |  |  | 0.007905 | 0.003216515972 | 1.0345975e-05
-0.006 | 0.004 | -0.001 | 0.007 | 0.02 |  |  |  | 0.007848 | 0.003215726357 | 1.0340896e-05
0.004 | -0.001 | 0.003 | 0.005 | 0.03 |  |  |  | 0.007851 | 0.003214467141 | 1.0332799e-05
0.001 | 0.006 | 0.006 | 0.009 | 0.04 |  |  |  | 0.007851 | 0.003214467141 | 1.0332799e-05
0.001 | 0.006 | 0 | 0.006 | 0.05 |  |  |  | 0.007908 | 0.003214270679 | 1.0331536e-05
0.002 | -0.001 | 0.008 | 0.009 | 0.06 |  |  |  | 0.007899 | 0.003213533725 | 1.0326799e-05
-0.001 | 0.004 | -0.005 | 0.007 | 0.07 |  |  |  | 0.00785 | 0.003213331604 | 1.03255e-05
0.004 | 0.011 | 0.006 | 0.013 | 0.08 |  |  |  | 0.007904 | 0.003212908962 | 1.0322784e-05
0.005 | 0.009 | 0.002 | 0.011 | 0.09 |  |  |  | 0.007855 | 0.003212783061 | 1.0321975e-05
0.004 | 0.008 | -0.005 | 0.01 | 0.1 |  |  |  | 0.0079 | 0.003212475681 | 1.032e-05
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

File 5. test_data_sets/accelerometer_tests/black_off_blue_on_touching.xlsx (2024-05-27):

RAW DATA |  |  |  |  | (scroll to 10s to view data) |  |  | (same as column FGH but sorted by value)
X (g) | Y (g) | Z (g) | Magnitude (g) | time (s) | 10s moving avg | 10s moving std | 10s moving var | 10s moving avg | 10s moving std | 10s moving var
-0.006 | 0.025 | 0.01 | 0.028 | 0.01 |  |  |  | 0.018385 | 0.006969130147 | 4.8568775e-05
0.005 | 0.002 | 0.002 | 0.006 | 0.02 |  |  |  | 0.018386 | 0.006969003085 | 4.8567004e-05
-0.003 | -0.009 | -0.003 | 0.01 | 0.03 |  |  |  | 0.018394 | 0.006968985866 | 4.8566764e-05
0.005 | -0.007 | 0.014 | 0.017 | 0.04 |  |  |  | 0.018381 | 0.00696748441 | 4.8545839e-05
-0.011 | 0.023 | 0.009 | 0.027 | 0.05 |  |  |  | 0.018403 | 0.006965241633 | 4.8514591e-05
-0.004 | 0.011 | -0.004 | 0.012 | 0.06 |  |  |  | 0.018393 | 0.006964520874 | 4.8504551e-05
0 | -0.004 | -0.004 | 0.005 | 0.07 |  |  |  | 0.018391 | 0.006964489859 | 4.8504119e-05
0.005 | -0.016 | -0.012 | 0.021 | 0.08 |  |  |  | 0.0184 | 0.006962327197 | 4.8474e-05
-0.015 | 0.013 | 0.008 | 0.022 | 0.09 |  |  |  | 0.018406 | 0.006961979891 | 4.8469164e-05
0.001 | 0.017 | 0.001 | 0.017 | 0.1 |  |  |  | 0.018389 | 0.006961873239 | 4.8467679e-05
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

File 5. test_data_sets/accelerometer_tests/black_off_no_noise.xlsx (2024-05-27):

RAW DATA |  |  |  |  | (scroll to 10s to view data) |  |  | (same as column FGH but sorted by value)
X (g) | Y (g) | Z (g) | Magnitude (g) | time (s) | 10s moving avg | 10s moving std | 10s moving var | 10s moving avg | 10s moving std | 10s moving var
-0.003 | -0.005 | 0.001 | 0.006 | 0.01 |  |  |  | 0.005623 | 0.002354330266 | 5.542871e-06
-0.003 | 0.001 | 0 | 0.003 | 0.02 |  |  |  | 0.005627 | 0.002352843174 | 5.535871e-06
-0.006 | 0.005 | -0.002 | 0.008 | 0.03 |  |  |  | 0.005626 | 0.002352471891 | 5.534124e-06
0.005 | 0.003 | 0.004 | 0.008 | 0.04 |  |  |  | 0.00563 | 0.00235097852 | 5.5271e-06
-0.003 | 0.003 | -0.001 | 0.004 | 0.05 |  |  |  | 0.005631 | 0.00235092301 | 5.526839e-06
0.003 | 0.003 | -0.002 | 0.005 | 0.06 |  |  |  | 0.005625 | 0.002349973404 | 5.522375e-06
-0.001 | 0.005 | -0.002 | 0.005 | 0.07 |  |  |  | 0.005625 | 0.002349973404 | 5.522375e-06
-0.002 | 0.003 | -0.004 | 0.006 | 0.08 |  |  |  | 0.005619 | 0.002349859357 | 5.521839e-06
0.002 | 0.001 | -0.003 | 0.004 | 0.09 |  |  |  | 0.005619 | 0.002349859357 | 5.521839e-06
-0.001 | 0.007 | 0 | 0.007 | 0.1 |  |  |  | 0.005619 | 0.002349859357 | 5.521839e-06
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

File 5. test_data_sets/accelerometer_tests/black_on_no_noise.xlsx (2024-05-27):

RAW DATA |  |  |  |  | (scroll to 10s to view data) |  |  | (same as column FGH but sorted by value)
X (g) | Y (g) | Z (g) | Magnitude (g) | time (s) | 10s moving avg | 10s moving std | 10s moving var | 10s moving avg | 10s moving std | 10s moving var
-0.109 | -0.14 | -0.212 | 0.276 | 0.01 |  |  |  | 0.213068 | 0.07618126657 | 0.005803585376
0.074 | -0.168 | -0.025 | 0.186 | 0.02 |  |  |  | 0.212893 | 0.07621222704 | 0.005808303551
0.067 | -0.007 | -0.199 | 0.21 | 0.03 |  |  |  | 0.212863 | 0.07626857958 | 0.005816896231
0.029 | 0.239 | 0.226 | 0.33 | 0.04 |  |  |  | 0.212895 | 0.07631049715 | 0.005823291975
-0.108 | 0.034 | -0.072 | 0.134 | 0.05 |  |  |  | 0.213002 | 0.07631127044 | 0.005823409996
0.032 | -0.103 | 0.028 | 0.112 | 0.06 |  |  |  | 0.212788 | 0.07631182776 | 0.005823495056
0.039 | -0.099 | -0.151 | 0.185 | 0.07 |  |  |  | 0.212931 | 0.07633124026 | 0.005826458239
0.024 | 0.155 | 0.238 | 0.285 | 0.08 |  |  |  | 0.212925 | 0.07633475863 | 0.005826995375
-0.056 | 0.076 | -0.086 | 0.127 | 0.09 |  |  |  | 0.21281 | 0.07633650437 | 0.0058272619
0.015 | -0.136 | 0.008 | 0.137 | 0.1 |  |  |  | 0.21299 | 0.07641215806 | 0.0058388179
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

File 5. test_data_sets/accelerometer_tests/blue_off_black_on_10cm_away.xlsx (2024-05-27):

RAW DATA |  |  |  |  | (scroll to 10s to view data) |  |  | (same as column FGH but sorted by value)
X (g) | Y (g) | Z (g) | Magnitude (g) | time (s) | 10s moving avg | 10s moving std | 10s moving var | 10s moving avg | 10s moving std | 10s moving var
0.005 | 0.009 | -0.003 | 0.011 | 0.01 |  |  |  | 0.028999 | 0.01868638539 | 0.000349180999
-0.006 | 0.012 | 0.003 | 0.013 | 0.02 |  |  |  | 0.02902 | 0.01868356497 | 0.0003490756
-0.028 | -0.003 | -0.015 | 0.032 | 0.03 |  |  |  | 0.02903 | 0.01867289747 | 0.0003486771
0.012 | -0.018 | 0.014 | 0.026 | 0.04 |  |  |  | 0.029032 | 0.01867262638 | 0.000348666976
0 | 0.013 | -0.007 | 0.015 | 0.05 |  |  |  | 0.029032 | 0.01867171594 | 0.000348632976
0.007 | 0.011 | 0.017 | 0.021 | 0.06 |  |  |  | 0.029039 | 0.01866589079 | 0.000348415479
-0.034 | 0.001 | -0.035 | 0.048 | 0.07 |  |  |  | 0.029016 | 0.01865383993 | 0.000347965744
0.013 | -0.02 | 0.011 | 0.026 | 0.08 |  |  |  | 0.028986 | 0.01865319822 | 0.000347941804
-0.002 | 0.01 | -0.009 | 0.013 | 0.09 |  |  |  | 0.029004 | 0.01865105852 | 0.000347861984
0.023 | 0.012 | 0.015 | 0.03 | 0.1 |  |  |  | 0.029005 | 0.01865054892 | 0.000347842975
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

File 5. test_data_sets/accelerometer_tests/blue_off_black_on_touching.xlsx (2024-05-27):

RAW DATA |  |  |  |  | (scroll to 10s to view data) |  |  | (same as column FGH but sorted by value)
X (g) | Y (g) | Z (g) | Magnitude (g) | time (s) | 10s moving avg | 10s moving std | 10s moving var | 10s moving avg | 10s moving std | 10s moving var
-0.007 | 0.005 | -0.002 | 0.009 | 0.01 |  |  |  | 0.04689 | 0.02571979588 | 0.0006615079
0.035 | 0.014 | 0.005 | 0.038 | 0.02 |  |  |  | 0.046997 | 0.02570145893 | 0.000660564991
-0.044 | 0.007 | -0.022 | 0.049 | 0.03 |  |  |  | 0.046879 | 0.02569471461 | 0.000660218359
0.019 | -0.013 | 0.008 | 0.024 | 0.04 |  |  |  | 0.046925 | 0.02569200994 | 0.000660079375
0.006 | -0.002 | -0.016 | 0.017 | 0.05 |  |  |  | 0.046979 | 0.02568993108 | 0.000659972559
0.026 | 0.015 | 0.002 | 0.03 | 0.06 |  |  |  | 0.046933 | 0.02568650445 | 0.000659796511
-0.059 | 0.013 | -0.021 | 0.064 | 0.07 |  |  |  | 0.0469 | 0.02568524868 | 0.000659732
0.024 | -0.016 | 0.007 | 0.03 | 0.08 |  |  |  | 0.046772 | 0.0256823678 | 0.000659584016
0.012 | 0.001 | -0.019 | 0.023 | 0.09 |  |  |  | 0.046895 | 0.02568108204 | 0.000659517975
0.03 | 0.016 | 0.017 | 0.038 | 0.1 |  |  |  | 0.046973 | 0.02568093205 | 0.000659510271
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

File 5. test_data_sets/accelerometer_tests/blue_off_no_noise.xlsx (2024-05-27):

RAW DATA |  |  |  |  | (scroll to 10s to view data) |  |  | (same as column FGH but sorted by value)
X (g) | Y (g) | Z (g) | Magnitude (g) | time (s) | 10s moving avg | 10s moving std | 10s moving var | 10s moving avg | 10s moving std | 10s moving var
-0.003 | 0 | -0.001 | 0.148 | 0.01 |  |  |  | 0.005565 | 0.005623502023 | 3.1623775e-05
0.001 | 0.003 | -0.001 | 0.057 | 0.02 |  |  |  | 0.005566 | 0.005623312547 | 3.1621644e-05
0.001 | 0.003 | -0.001 | 0.043 | 0.03 |  |  |  | 0.005567 | 0.005623300721 | 3.1621511e-05
-0.002 | 0.005 | 0.005 | 0.042 | 0.04 |  |  |  | 0.005544 | 0.00562299422 | 3.1618064e-05
-0.005 | 0.005 | 0.004 | 0.03 | 0.05 |  |  |  | 0.005547 | 0.005622969945 | 3.1617791e-05
0 | 0 | 0.002 | 0.018 | 0.06 |  |  |  | 0.00556 | 0.005622846254 | 3.16164e-05
0.005 | 0.004 | -0.001 | 0.015 | 0.07 |  |  |  | 0.00555 | 0.005622410515 | 3.16115e-05
-0.003 | 0.006 | 0.003 | 0.014 | 0.08 |  |  |  | 0.005551 | 0.005622401533 | 3.1611399e-05
0 | 0.002 | 0.003 | 0.014 | 0.09 |  |  |  | 0.005562 | 0.005622290992 | 3.1610156e-05
-0.006 | -0.003 | -0.005 | 0.014 | 0.1 |  |  |  | 0.005591 | 0.005622252129 | 3.1609719e-05
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

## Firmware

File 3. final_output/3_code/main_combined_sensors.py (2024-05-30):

# micropython code for the pico
# combines the individual sensor codes main_acc.py and main_mic.py
# prints the accelerometer magnitude and the microphone volume unit
# results are recorded every 10ms
# calculate the offsets from offset_calibration.py

from machine import Pin, I2C, ADC
import utime
import time

# I2C setup for accelerometer
i2c = I2C(1, scl=Pin(3), sda=Pin(2), freq=400000)

# ICM-20948 I2C address
ICM20948_ADDR = 0x68

# Register addresses from the datasheet
REG_PWR_MGMT_1 = 0x06
REG_ACCEL_XOUT_H = 0x2D

# Initialize the ICM-20948
i2c.writeto_mem(ICM20948_ADDR, REG_PWR_MGMT_1, bytearray([0x01]))

# Sensitivity for ±2g (assuming we are using ±2g)
SENSITIVITY = 16384

# Offsets measured during calibration
offset_x = 0.001  # Replace with actual offset values
offset_y = -0.023  # Replace with actual offset values
offset_z = 0.075  # Replace with actual offset values

# Setup ADC (Analog to Digital Converter) on GPIO 26 (Pin 31) for microphone
mic = ADC(Pin(26))

# Button setup
button = Pin(15, Pin.IN, Pin.PULL_UP)

# Variables to find the peak-to-peak amplitude of AUD output
sample_time = 10

def read_calibrated_accel():
    data = i2c.readfrom_mem(ICM20948_ADDR, REG_ACCEL_XOUT_H, 6)
    accel_x = (data[0] << 8 | data[1])
    accel_y = (data[2] << 8 | data[3])
    accel_z = (data[4] << 8 | data[5])
    
    if accel_x >= 32768:
        accel_x -= 65536
    if accel_y >= 32768:
        accel_y -= 65536
    if accel_z >= 32768:
        accel_z -= 65536

    accel_x_g = accel_x / SENSITIVITY - offset_x - 1
    accel_y_g = accel_y / SENSITIVITY - offset_y
    accel_z_g = accel_z / SENSITIVITY - offset_z
    mag = (accel_x_g ** 2 + accel_y_g ** 2 + accel_z_g ** 2) ** 0.5
    return mag

# Function to find the Peak-to-Peak Amplitude for microphone
def find_ptp_amp():
    start_time = time.ticks_ms()  # Start of sample window
    max_amp = 0
    min_amp = 65535  # 16-bit resolution of Pico ADC

    # Find the max and min of the mic output within the 50 ms timeframe
    while time.ticks_diff(time.ticks_ms(), start_time) < sample_time:
        mic_out = mic.read_u16() >> 4  # Convert 16-bit reading to 12-bit
        if mic_out < 4096:  # prevent erroneous readings
            if mic_out > max_amp:
                max_amp = mic_out  # save only the max reading
            elif mic_out < min_amp:
                min_amp = mic_out  # save only the min reading

    ptp_amp = max_amp - min_amp  # (max amp) - (min amp) = peak-to-peak amplitude
    mic_out_volts = (ptp_amp * 3.3) / 4096  # Convert ADC into voltage

    return ptp_amp

# Volume Unit Meter function: map the PTP amplitude to a volume unit between 0 and 10.
def vu_meter(mic_amp):
    # Adjust the minimum and maximum values based on your requirements
    min_val = 50   # Adjust this value based on the minimum expected amplitude
    max_val = 3000 # Adjust this value based on the maximum expected amplitude

    # Map the mic peak-to-peak amplitude to a volume unit between 0 and 10.
    # Amplitude is used instead of voltage to give a larger (and more accurate) range for the map function.
    fill = (mic_amp - min_val) * 10 / (max_val - min_val)
    fill = max(0, min(fill, 10))  # Ensure the value is within 0-10 range

    return fill

# Main loop with combined output
while True:
    # Check if the button is pressed
    if button.value() == 0:  # Button is pressed
        print("BUTTON_PRESSED")
        time.sleep(0.5)  # Wait for 1 second before checking again
    else:
        # Read accelerometer data
        mag = read_calibrated_accel()
        
        # Read microphone data
        mic_output = find_ptp_amp()
        vu_value = vu_meter(mic_output)
        
        # Print only the accelerometer magnitude and microphone volume unit
        print('{:.3f},{:.2f}'.format(mag, vu_value))

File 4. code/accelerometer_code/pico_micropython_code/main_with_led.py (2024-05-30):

# this code performs the functions described in the interim report
# it calculates the rolling values of mean and sd
# and then lights up an LED depending on whether they both reach the desired threshold
# this code is run standalone and does not require python on the laptop
# ensure that the led is attached to the correct pin to match the code
# code to calibrate and remove offsets in combined_sensor_code\pico_micropython_code folder

from machine import Pin, I2C  # used to interact with the pico
import utime

# I2C setup
i2c = I2C(1, scl=Pin(3), sda=Pin(2), freq=400000)  # initializes the I2C bus on bus 1, with the clock on pin 3 and data on pin 2

# ICM-20948 I2C address
ICM20948_ADDR = 0x68

# Register addresses from the datasheet for power management and accelerometer data
REG_PWR_MGMT_1 = 0x06
REG_ACCEL_XOUT_H = 0x2D

# Initialize the ICM-20948 by writing to the power management register
i2c.writeto_mem(ICM20948_ADDR, REG_PWR_MGMT_1, bytearray([0x01]))

# Sensitivity for ±2g (assuming we are using ±2g, this can be adjusted)
SENSITIVITY = 16384

# Offsets measured during calibration
offset_x = 0.0  # Replace with actual offset values
offset_y = -0.02  # Replace with actual offset values
offset_z = 0.07  # Replace with actual offset values

# Buffer size
BUFFER_SIZE = 1000  # Size of the circular buffer

# Circular buffer to store the last 1000 magnitude values
mag_buffer = [0] * BUFFER_SIZE
buffer_index = 0
buffer_filled = False

# Variables to keep track of the sum and sum of squares of magnitudes
sum_mag = 0
sum_mag_squared = 0

# Initialize GPIO 15 as an output pin for the LED
led = Pin(15, Pin.OUT)

def read_calibrated_accel():
    # Reads the current accelerometer output
    data = i2c.readfrom_mem(ICM20948_ADDR, REG_ACCEL_XOUT_H, 6)
    
    # Combines the high and low bytes to form a 16-bit output
    accel_x = (data[0] << 8 | data[1])
    accel_y = (data[2] << 8 | data[3])
    accel_z = (data[4] << 8 | data[5])
    
    # Adjusts for the two's complement representation
    if accel_x >= 32768:
        accel_x -= 65536
    if accel_y >= 32768:
        accel_y -= 65536
    if accel_z >= 32768:
        accel_z -= 65536

    # Convert raw values to g-forces and apply offsets
    accel_x_g = accel_x / SENSITIVITY - offset_x - 1
    accel_y_g = accel_y / SENSITIVITY - offset_y
    accel_z_g = accel_z / SENSITIVITY - offset_z
    mag = (accel_x_g ** 2 + accel_y_g ** 2 + accel_z_g ** 2) ** 0.5
    return accel_x_g, accel_y_g, accel_z_g, mag

def update_stats(new_value):
    # Update statistics for the circular buffer of magnitudes
    global buffer_index, buffer_filled, sum_mag, sum_mag_squared
    
    old_value = mag_buffer[buffer_index]
    
    # Update the buffer with the new value
    mag_buffer[buffer_index] = new_value
    buffer_index = (buffer_index + 1) % BUFFER_SIZE
    if buffer_index == 0:
        buffer_filled = True

    # Update sums
    sum_mag += new_value - old_value
    sum_mag_squared += new_value ** 2 - old_value ** 2
    
    count = BUFFER_SIZE if buffer_filled else buffer_index
    mean = sum_mag / count
    standard_dev = ((sum_mag_squared / count) - (mean ** 2)) ** 0.5
    return mean, standard_dev

# Desired loop interval in milliseconds
desired_interval_ms = 10

# Main loop to read accelerometer data and update statistics
while True:
    start_time = utime.ticks_ms()
    
    accel_x_g, accel_y_g, accel_z_g, mag = read_calibrated_accel()
    print('{:.3f},{:.3f},{:.3f},{:.3f}'.format(accel_x_g, accel_y_g, accel_z_g, mag))
    
    mean, standard_dev = update_stats(mag)
    
    if buffer_filled:
        print('Mean: {:.6f}, SD: {:.6f}'.format(mean, standard_dev))
        if mean > 0.04 and standard_dev > 0.02:
            led.value(1)  # Turn the LED on
        else:
            led.value(0)  # Turn the LED off
    
    elapsed_time = utime.ticks_diff(utime.ticks_ms(), start_time)
    sleep_time = desired_interval_ms - elapsed_time  # Calculate remaining time to sleep
    if sleep_time > 0:
        utime.sleep_ms(sleep_time)
    else:
        # If processing took longer than the desired interval, print a warning
        print("Warning: Processing is slower than the desired interval")

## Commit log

2024-05-22 LED code
2024-05-23 STL file for clip
    [4Clip2 - Clip1-1.STL]
2024-05-24 screenshots of interim prototype
2024-05-24 prototype updates
2024-05-24 updated prototype section
2024-05-24 led circuit info
2024-05-24 photo of LED circuit
2024-05-24 Rename WhatsApp Image 2024-05-24 at 18.05.01_f64ef5db.jpg to led_circuit.jpg
2024-05-24 led circuit photo
2024-05-26 Rename 4Clip2 - Clip1-1.STL to interim/assets/4Clip2 - Clip1-1.STL
    [4Clip2 - Clip1-1.STL]
2024-05-26 Rename 4Clip2 - Clip1-1.STL to clip.STL
    [clip.STL]
2024-05-27 organising and rewriting the read me
    [clip.STL]
2024-05-27 editing the read me
    [clip.STL]
2024-05-27 old data
    [baseline_on.xlsx, black_off_blue_10cm.xlsx, black_off_blue_touching.xlsx, black_off_no_noise.xlsx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]
2024-05-27 adding test data
    [black_off_blue_on_10cm_away.xlsx, black_off_blue_on_touching.xlsx, black_off_no_noise.xlsx, black_on_no_noise.xlsx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]
2024-05-30 added combined sensor code
2024-05-30 test data new folders
    [black_off_blue_on_10cm_away.xlsx, black_off_blue_on_touching.xlsx, black_off_no_noise.xlsx, black_on_no_noise.xlsx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]
2024-05-30 adding microphone test data
    [black_on_near_blue.xlsx, black_on_near_blue_foam.xlsx, blue_on.xlsx, blue_on_foam.xlsx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]
2024-05-30 combined sensor test results
    [blue_on.xlsx, carrying_concentrator.xlsx, no_noise.xlsx, rolling_concentrator.xlsx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]
2024-05-30 updating read me's and creating new test data folders
    [black_on_near_blue.xlsx, black_on_near_blue_foam.xlsx, blue_on.xlsx, blue_on_foam.xlsx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]
2024-06-03 update circuit
2024-06-03 stl file
    [clip copy.STL]
2024-06-03 Rename clip copy.STL to clip.STL
    [clip.STL]
2024-06-03 combined sensor tests
2024-06-03 final prototype
2024-06-03 updated prototype
2024-06-03 rename folders
    [black_off_blue_on_10cm_away.xlsx, black_off_blue_on_touching.xlsx, black_off_no_noise.xlsx, black_on_near_blue.xlsx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]
2024-06-03 re order final output
    [clip.STL]
2024-06-03 para breaks
2024-06-03 our prototype
2024-06-04 finilised prototype
2024-06-04 Rename Oxygen Concentrator Monitoring Device.pdf to final_presentation_slides.pdf
